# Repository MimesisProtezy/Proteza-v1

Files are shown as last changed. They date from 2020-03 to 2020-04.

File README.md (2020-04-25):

# Proteza-v1 🦾



To jest repozytorium ze wszystkimi plikami niezbędnymi do wykonania protezy bionicznej, która powstała w ramach olimpiady Zwolnieni z Teorii.<meta name="google-site-verification" content="7BU-_dNy4WX7rQMSjwO5azxOfN85TyO-x6rC1iT2Cm4" />

## Wstęp
Profesjonalne protezy bioniczne dostępne na rynku potrafią kosztować dzisiątki tysięcy złotych. Postanowiliśmy zaproponować znacznie tańszą alternatywę o podobnej funkcjonalności.
Pamiętaj, że jest to pierwsza wersja tego urządzenia i będzie ono udoskanalane.
W pierwszym prototypie zdecydowaliśmy się na podzielenie projektu na dwie części: właściwą protezę oraz opaskę sterującą. W protezie znajdują się serwa, baterie i ESP32, które wszystkim steruje, a w opasce sensory EMG, mała bateria oraz kolejne ESP32 odpowiedzialne za pobieranie danych z sensorów i przekazywania ich do protezy.

# Przygotowania

#### Narzędzia niezbędne do wykonania protezy ⚒️

* wkręty 2,5mm (często trzeba je przyciąć do pożądanej długości)
* śrubki 3mm
* nakrętki 3mm
* śrubokręt albo wkrętarka
* pilniki (do wykańczania wydruków)
* klej błyskawiczny np. kropelka (lub aceton w przypadku wydruku z ABS)
* żyłka wędkarska (najlepiej nie nylonowe, ponieważ ulegają one rozciągnięciu)
* lutownica
* drukarka 3D (my drukowaliśmy na Enderze 3)

#### Komponenty elektroniczne protezy 🦾

* [ESP32](https://botland.com.pl/pl/moduly-wifi/8893-esp32-wifi-bt-42-platforma-z-modulem-esp-wroom-32-zgodny-z-esp32-devkit.html) x2
* [Sensor emg](https://botland.com.pl/pl/czujniki-medyczne/5978-myoware-muscle-sensor-czujnik-do-pomiaru-aktywnosci-miesni-emg-869249000109.html) x3 - odczyt sygnałów elektrycznych z mięśni
* [Elektrody biomedyczne](https://botland.com.pl/pl/czujniki-medyczne/2604-elektrody-biomedyczne-10szt.html) x 2 (lub więcej) opakowań
* [Przewody do elektrod](https://botland.com.pl/pl/czujniki-medyczne/2605-przewody-do-elektrod-biomedycznych.html)
* [Powerboost](https://botland.com.pl/pl/ladowarki-lipol-moduly/10171-dfrobot-mp2636-power-booster-charger-module-modul-ladowarki-li-ionli-pol-6v25a.html) - odpowiedzialny za zasilanie oraz ładowanie protezy
* [Serwo](https://botland.com.pl/pl/serwa-typu-micro/10311-serwo-feetech-wing-ft3325m-micro.html) x4 - zdecydowaliśmy się na ten produkt ponieważ najlepiej spełnia parametry wystarczającej siły, głośności pracy oraz ceny
* [Zasilacz](https://botland.com.pl/pl/zasilacze-do-raspberry-pi-4b/7820-zasilacz-extreme-5v-31a-ze-zlaczem-usb-c-dla-raspberry-pi-4b-5901445617509.html) - można użyć innego zasilacza o podobnych parametrach
* [Złącze usb typu C do płytki stykowej](https://botland.com.pl/pl/akcesoria-do-plytek-stykowych/12658-pololu-usb-20-typ-c-zlacze-do-plytki-stykowej.html) x2 - umożliwa łatwy dostęp do portów ładowania i programowania
* [Ogniwa li-pol 2200mah](https://botland.com.pl/pl/akumulatory-li-pol/1313-ogniwo-li-pol-redox-2200mah-20c-1s-37v-90009947.html) x3
* [Gniazdo jack](https://botland.com.pl/pl/przewody-i-zlacza-audio/2734-gniazdo-jack-35-mm-stereo-zenskie-jy039-5p.html) x3 - umożliwa łatwe podłączenie przewodów elektrod

#### Komponenty elektroniczne opaski sterującej 🎛️

* [ESP32](https://botland.com.pl/pl/moduly-wifi/8893-esp32-wifi-bt-42-platforma-z-modulem-esp-wroom-32-zgodny-z-esp32-devkit.html)
* [Akumulator li-pol 1200mah](https://botland.com.pl/pl/akumulatory-li-pol/14159-akumulator-li-pol-akyga-1200mah-1s-37v-zlacze-jst-bec-gniazdo-50x34x6mm.html) - mały pobór energii opaski sterującej umożliwia umieszczenie mniejszej baterii, co pozwala na większy komfort użytkowania
* [Gniazdo do akumulatorów li-pol](https://botland.com.pl/pl/akcesoria-do-akumulatorow/1320-gniazdo-jst-bec-do-akumulatorow-li-pol.html) opaska jest ładowana przy użyciu PowerBoosta z protezy. To gniazdo usprawnia proces podłączania opaski do ładowania.

#### Pliki 3D do wydruku 🖨️

* [Dłoń](https://github.com/MimesisProtezy/Proteza-v1/tree/master/STLs/D%C5%82o%C5%84) - folder ze wszystkimi plikami potrzebnymi do wydrukowania dłoni protezy (można je pobrać także ze strony inmoov.fr)
* [Przedramię](https://github.com/MimesisProtezy/Proteza-v1/tree/master/STLs/Przedrami%C4%99) - folder z częściami przedramienia
* [Obudowa na baterie](https://github.com/MimesisProtezy/Proteza-v1/tree/master/STLs/Battery%20holder) - obudowa służąca do przymocowania baterii wewnątrz przedramienia
* [Obudowa na serwa](https://github.com/MimesisProtezy/Proteza-v1/tree/master/STLs/Servo%20holder) - obudowa służaca do przymocowania serw wewnątrz przedramienia
* [Nadgarstek](https://github.com/MimesisProtezy/Proteza-v1/blob/master/STLs/Wrist.stl) - umożliwia połączenie dłoni z przedramieniem
* [Nakładka na serwo](https://github.com/MimesisProtezy/Proteza-v1/blob/master/STLs/Servo%20pulley.stl) x4 - do tej częsci przywiązywane będą żyłki odpowiedzialne za ruch palców

# Wykonanie

#### Dłoń
Model dłoni został zbudowany w oparciu o projekt [InMoov](http://inmoov.fr/) dlatego zachęcamy do kierowania się ich fantastyczną instrukcją składania [dłoni](http://inmoov.fr/hand-and-forarm/) oraz [palców](http://inmoov.fr/finger-starter/)

#### Przedramię

Proces składania przedramienia należy rozpocząć od wydrukowania wszystkich niezbędnych części ([Przedramię](https://github.com/MimesisProtezy/Proteza-v1/tree/master/STLs/Przedrami%C4%99), [Obudowa na baterie](https://github.com/MimesisProtezy/Proteza-v1/tree/master/STLs/Battery%20holder), [Obudowa na serwa](https://github.com/MimesisProtezy/Proteza-v1/tree/master/STLs/Servo%20holder), [Nadgarstek](https://github.com/MimesisProtezy/Proteza-v1/blob/master/STLs/Wrist.stl)). Niektóre części, takie jak przedramię oraz obudowa na serwa będą wymagały drukowania z supportami, które po wydrukowaniu należy usunąć.

Kolejnym krokiem jest połączenie części obudowy na serwa w sposób przedstawiony na zdjęciu poniżej. Do złączenia części można użyć kleju szybkoschnącego takiego jak kropelka albo żywicy 5-minutowej.



Następnie na zębatki w serwach należy nałożyć [nakładki](https://github.com/MimesisProtezy/Proteza-v1/blob/master/STLs/Servo%20pulley.stl) i dokręcić je dołączonymi do serw śrubkami. Później wszystkie serwa przykręcamy do wydrukowanej i sklejonej wcześniej obudowy w sposób przedstawiony poniżej. Należy do tego użyć przyciętych do odpowiedniej długości 2.5 milimetrowych wkrętów. Złącza wychodzące z serw należy przeprowadzić przez odpowiednie otwory w obudowie.



Kolejnym krokiem jest przykręcenie obudowy na serwa wraz z zamontowanymi serwami w obudowie przedramienia. Należy użyć do tego pięciu 2.5 milimetrowych wkrętów.



W tym momencie można przejść do złożenia obudowy na akumulatory. Pliki części obudowy na akumulatory zostały ponumerowane od góry do dołu, aby ułatwić złożenie. Poszczególne części należy połączyć wkrętami, wkręcając je przez wystające otwory montażowe. Oprócz tego części 1 i 2, 3 i 4, 5 i 6 należy skleić klejem szybkoschnącym.



Po umieszczeniu akumulatorów w obudowie należy zlutować je równolegle. W tym momencie warto jest też przylutować powerboost'a do równolegle połączonych akumulatorów, mając na uwadze długość przewodów niezbędną do połączenia powerboost'a z akumulatorami, gdy będą już umieszczone w obudowie. Przed umieszczeniem akumulatorów w obudowie przedramienia należy przykręcić dwa [złącza USB typu C](https://botland.com.pl/pl/akcesoria-do-plytek-stykowych/12658-pololu-usb-20-typ-c-zlacze-do-plytki-stykowej.html) w sposób pokazany na zdjęciu poniżej. Nad złączami USB przykręcamy powerboost'a za pomocą jednego wkręta.



Do jednego złącza USB typu C należy przylutować kabel zakończony z drugiej strony złączem USB typu A. Koniec kabla zakończony USB typu A podłączamy do portu USB w powerboost'cie. Dzięki temu jesteśmy w stanie w łatwy sposób ładować akumulatory w protezie poprzez podłączenie ładowarki zakończonej USB typu C. Przy lutowaniu kabla USB do złącza USB typu C w protezie nie jest konieczne łączenie wszystkich pinów. Wystarczy połączyć te odpowiedzialne za przesył prądu a nie danych (+5v i GND).

Do drugiego złącza typu C umieszczonego w protezie lutujemy kabel zakończony z drugiej strony złączem micro USB. Podłączamy go do portu USB w esp32. Dzięki temu będziemy w stanie programować esp32 podłączając się do niego w łatwy sposób. W tym wypadku musimy przylutować piny odpowiedzialne za przesył prądu i danych (+5v, D-, D+, GND).

Następnie możemy przykręcić wcześniej złożoną obudowę na akumulatory do protezy, w sposób pokazany na zdjęciu poniżej. Będą do tego potrzebne trzy wkręty. 



WIP

#### Schemat elektroniki w przedramieniu



#### Opaska

Wszystkie elementy są połączone kablami według schematu i schowane w opasce z odpowiednimi wyprowadzeniami do przymocowania elektrod do sensorów EMG.

#### Schemat elektroniki w opasce



# Projekt realizowany w ramach olimpiady


# Sponsor projektu
 

# Patroni medialni
         

# Partnerzy
                        



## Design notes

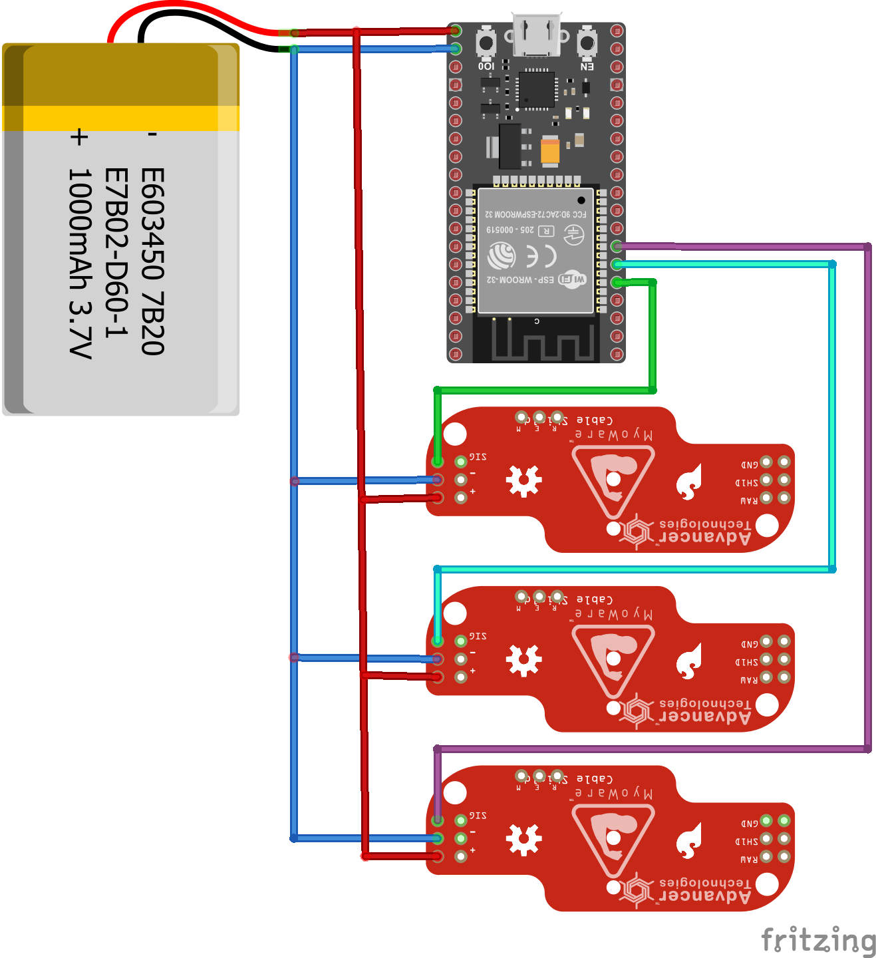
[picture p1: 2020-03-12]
schematics/Server_side_scheme.png

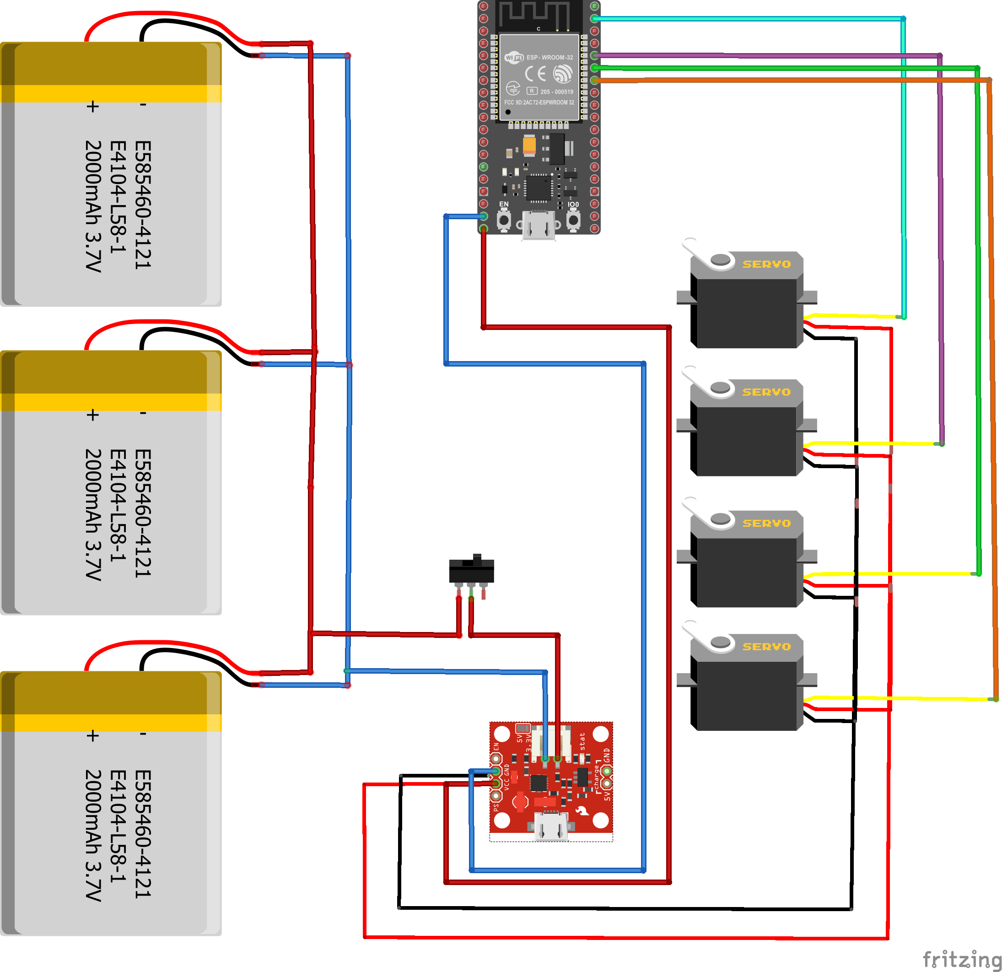
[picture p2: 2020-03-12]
schematics/Client_side_scheme.png

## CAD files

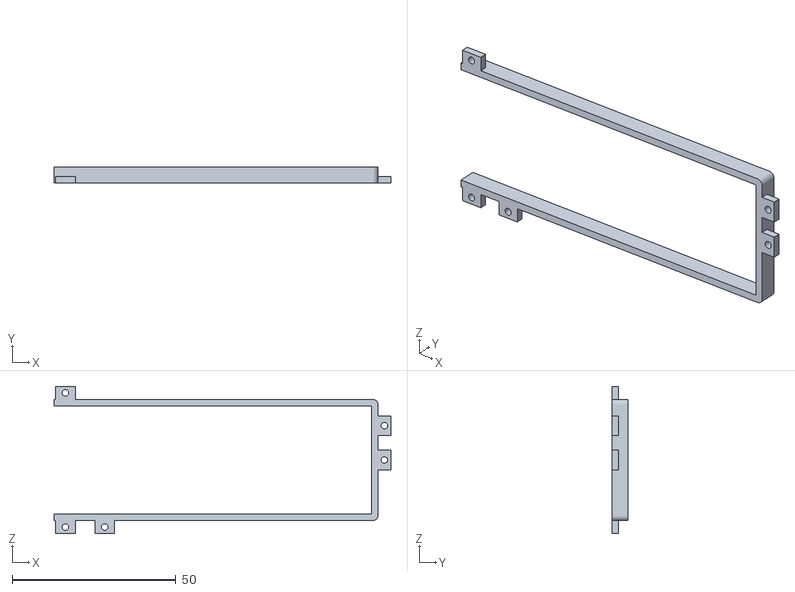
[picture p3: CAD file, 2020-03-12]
STLs/Battery holder/2.stl
103.0 x 5.00 x 45.0

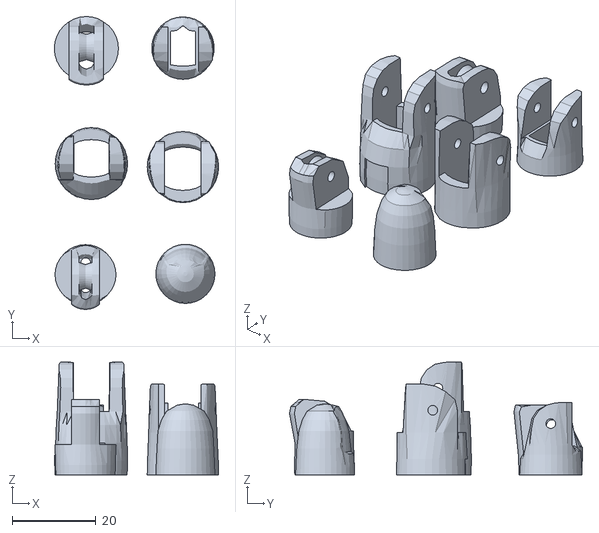
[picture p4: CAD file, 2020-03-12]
STLs/Dłoń/Index3.stl
39.4 x 70.2 x 27.0

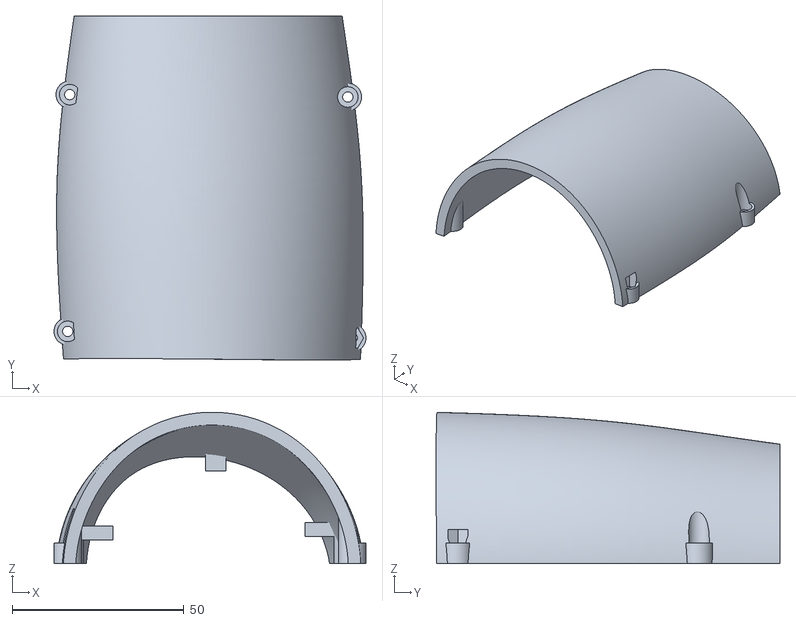
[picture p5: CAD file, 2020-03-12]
STLs/Przedramię/Shell_2.stl
90.9 x 100.2 x 44.1

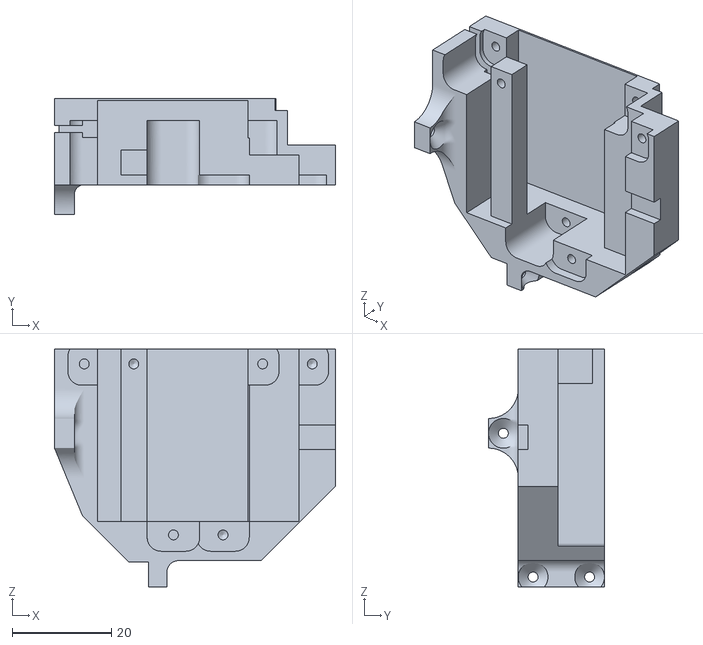
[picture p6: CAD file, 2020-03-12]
STLs/Servo holder/2.stl
56.7 x 23.4 x 48.0

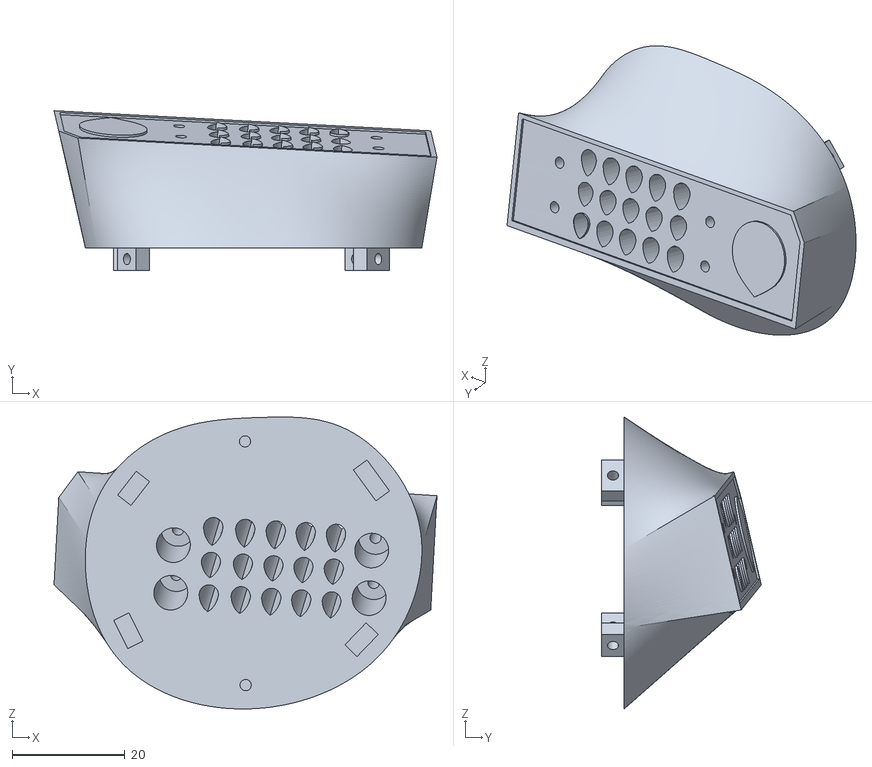
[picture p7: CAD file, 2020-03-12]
STLs/Wrist.stl
68.0 x 28.4 x 51.9

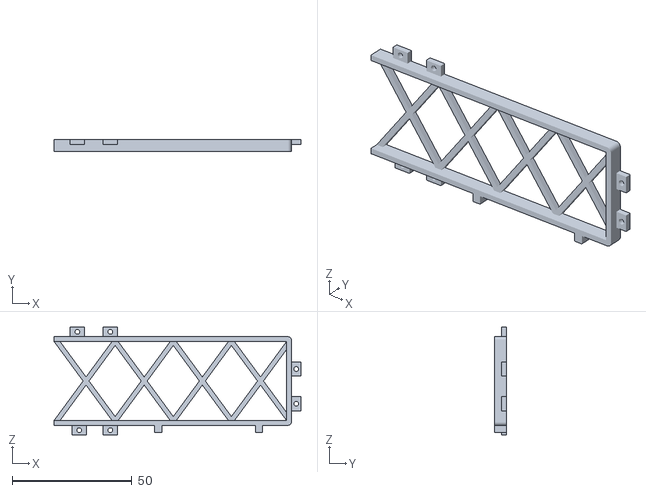
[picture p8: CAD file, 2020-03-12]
STLs/Battery holder/5.stl
103.0 x 5.00 x 45.0

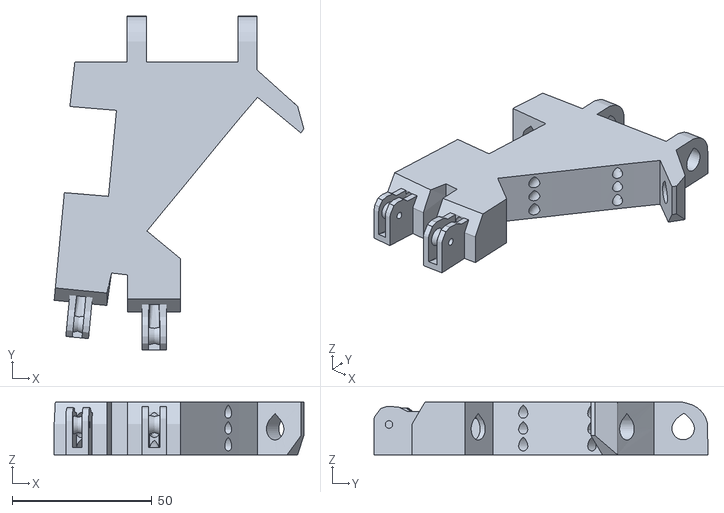
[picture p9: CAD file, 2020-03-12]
STLs/Dłoń/WristlargeV4 (1).stl
89.2 x 119.4 x 18.9

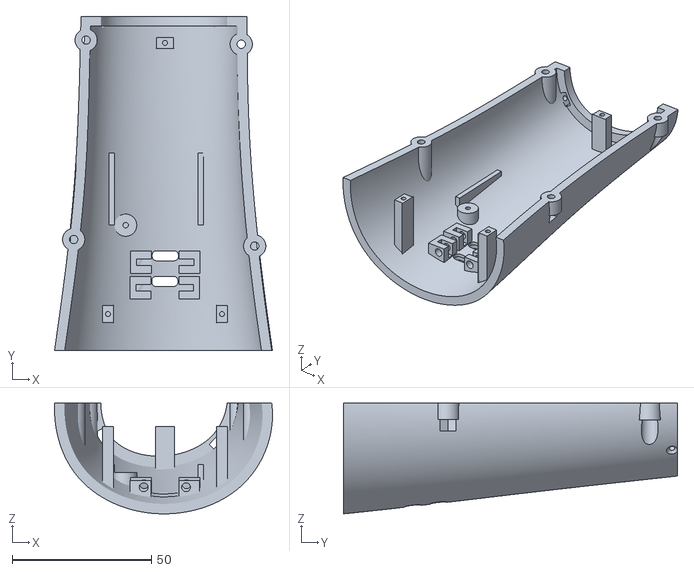
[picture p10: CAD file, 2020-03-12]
STLs/Przedramię/Shell_1 (1).stl
78.4 x 120.1 x 39.8

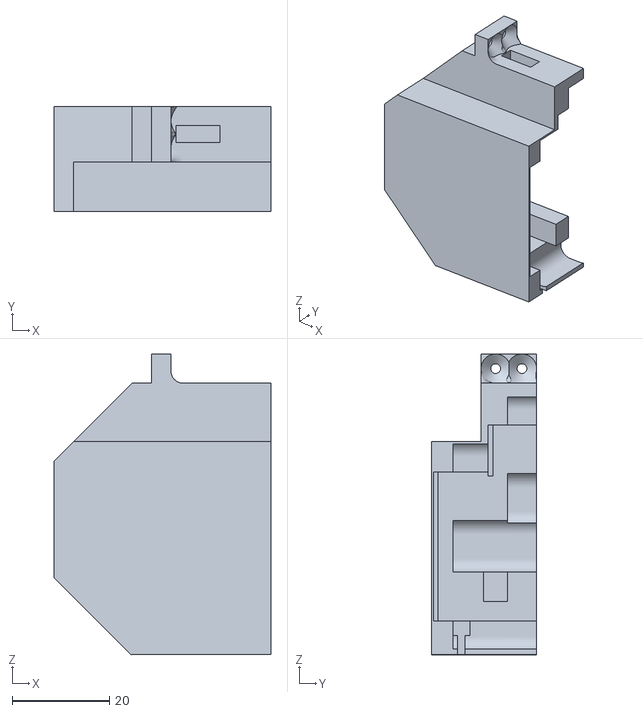
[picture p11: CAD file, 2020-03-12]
STLs/Servo holder/1.stl
44.5 x 21.6 x 61.8

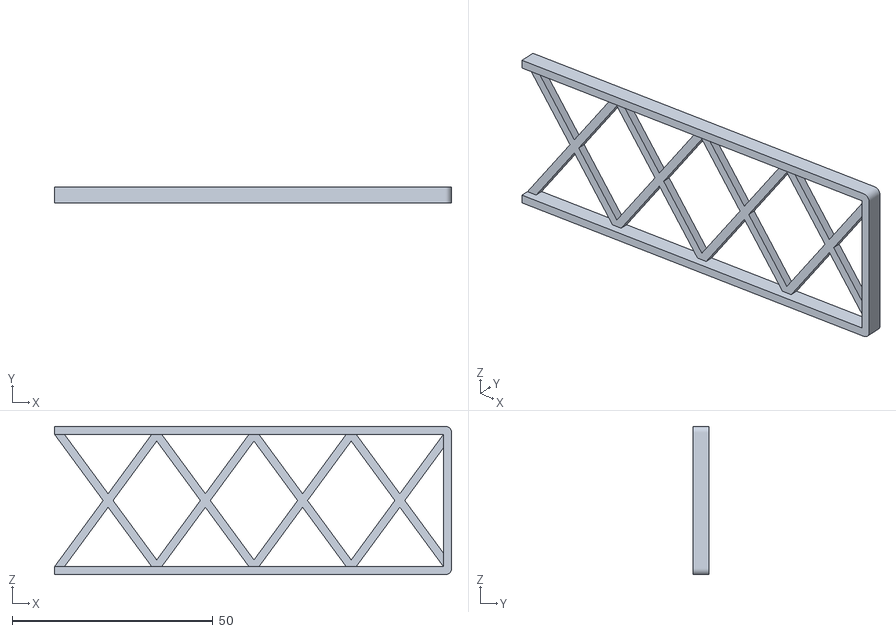
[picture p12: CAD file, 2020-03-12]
STLs/Battery holder/1.stl
99.0 x 4.00 x 37.0

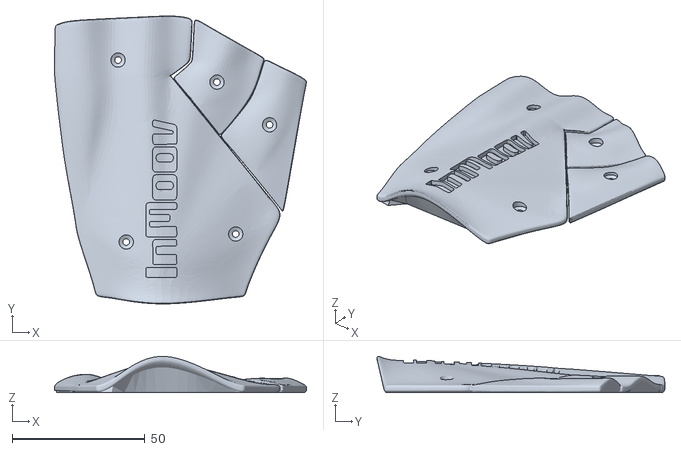
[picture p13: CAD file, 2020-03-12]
STLs/Dłoń/topsurface6.stl
94.8 x 108.3 x 13.7

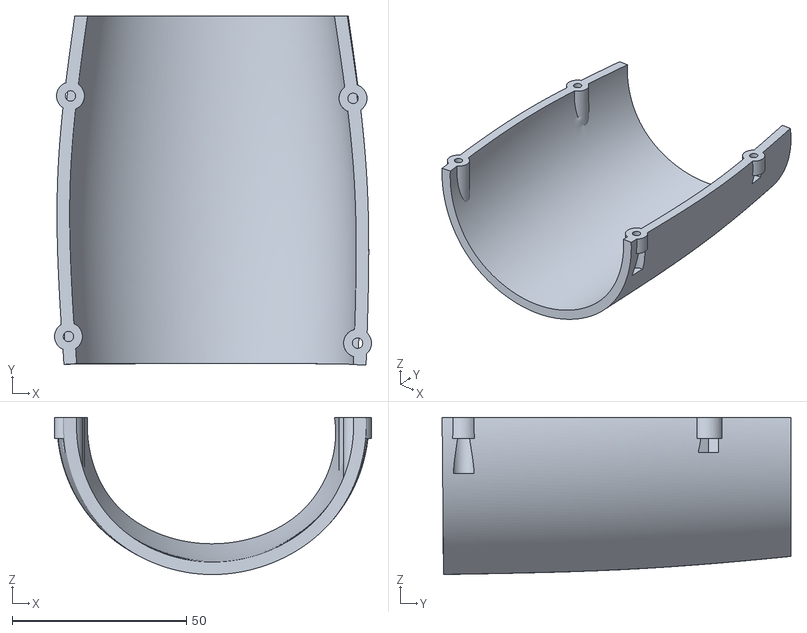
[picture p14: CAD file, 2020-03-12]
STLs/Przedramię/Shell_1.stl
90.9 x 100.0 x 45.0

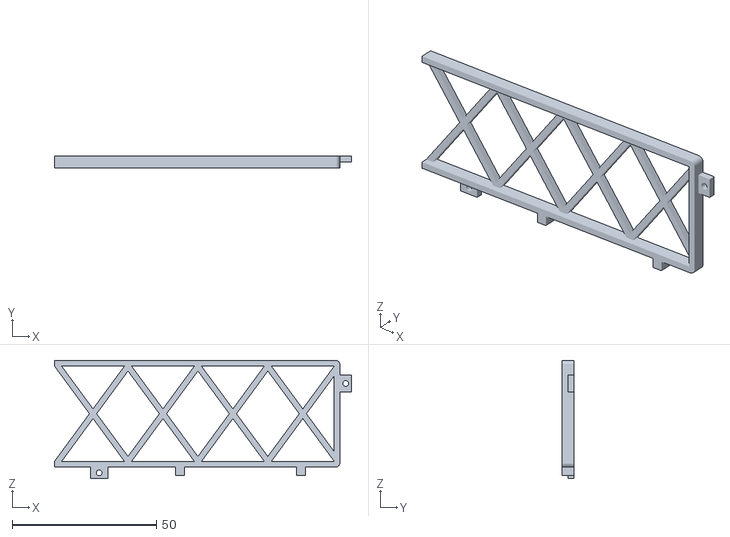
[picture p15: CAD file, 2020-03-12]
STLs/Battery holder/3.stl
103.0 x 4.00 x 41.0

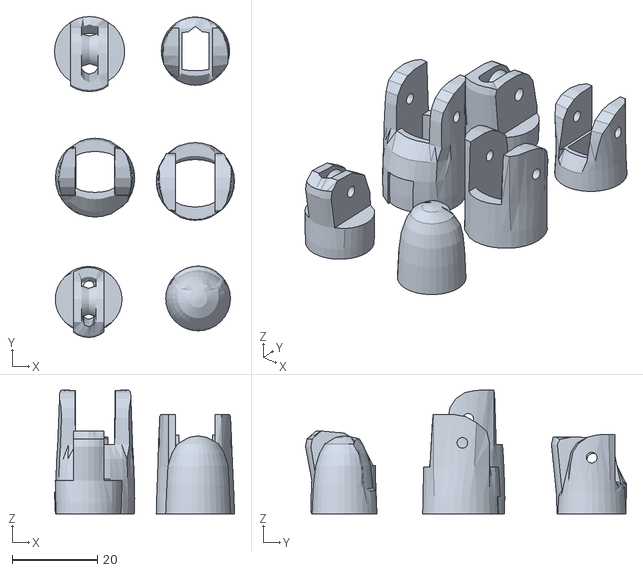
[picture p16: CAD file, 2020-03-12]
STLs/Dłoń/Majeure3 (1).stl
42.2 x 75.2 x 29.0

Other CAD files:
STLs/Przedramię/Shell_2 (1).stl
STLs/Battery holder/7.stl
STLs/Dłoń/Auriculaire3.stl
STLs/Battery holder/6.stl
STLs/Battery holder/4.stl
STLs/Dłoń/Bolt_entretoise7 (1).stl
STLs/Dłoń/WristsmallV4 (3).stl
STLs/Dłoń/coverfinger1 (4).stl
STLs/Dłoń/ringfinger3.stl
STLs/Dłoń/thumb5 (2).stl

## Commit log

2020-02-29 Add files via upload
    Code dedicated to operating a band which is responsible for readouts of EMG signals and passing them via wifi to another ESP32.
2020-02-29 server_side
    Code responsible for providing readouts from EMGs to another ESP32 via wifi.
2020-03-12 Modele 3D potrzebne do zbudowania protezy bionicznej
    Ten folder zawiera wszystkie pliki potrzebne do wydrukowania naszego pierwszego prototypu protezy bionicznej
    [1.stl, 2.stl, 3.stl, 4.stl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]
2020-03-12 Części przedramienia
    [Shell_1 (1).stl, Shell_1.stl, Shell_2 (1).stl, Shell_2.stl]
2020-03-12 Dodane części dłoni
    [Auriculaire3.stl, Bolt_entretoise7 (1).stl, Index3.stl, Majeure3 (1).stl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]
